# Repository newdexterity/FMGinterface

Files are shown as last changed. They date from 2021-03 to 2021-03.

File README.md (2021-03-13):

# A Wearable, Open-Source, Lightweight Forcemyography Armband: On Intuitive, Robust Muscle-Machine Interfaces
## Repository Contents
*	CAD files of the FSR based armband
*	ROS package to interface with the armband

## Force Sensitive Resistors based Armband

With an increasing number of robotic and prosthetic devices, there is a need for intuitive interfaces which enable the user to efficiently interact with them. The conventional interfaces are generally bulky and unsuitable for dynamic and unstructured environments. An alternative to the traditional interfaces is the class of Muscle-Machine Interfaces (MuMIs) that allow the user to have an embodied interaction with the devices they are controlling. In this work, we present a wearable, lightweight, FMG based armband for Human-Machine Interaction fabricated entirely out of 3D-printed parts and silicone components. The armband uses six force sensing units, each housing an FSR sensor. The capabilities of the armband are evaluated while decoding four different gestures (pinch, power, tripod, extension) and rest state and its performance is compared with a state-of-the-art electromyography (EMG) bioamplifier. The decoding performance of the decoding models trained on the data acquired from the armband is significantly better than the performance of the models trained on raw EMG data. The hardware design and the related processing software, are disseminated in an open-source manner.

### Components of the Band

The FMG band can be broken down into several smaller modules; the central control module, the strap module, and sensing modules. These components can be seen in Figure below. In total, there are currently six sensing modules evenly spaced around approximately 320˚ of the strap.

<p align="center">
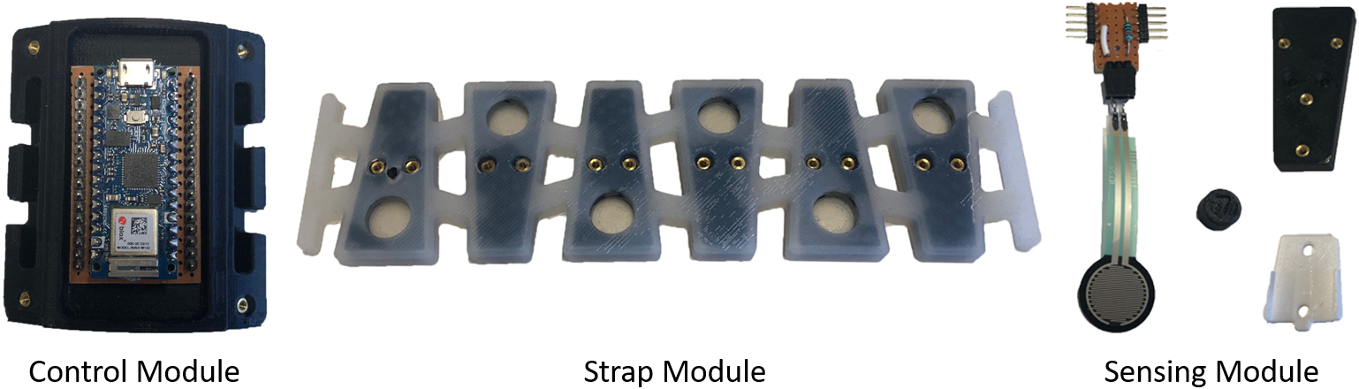
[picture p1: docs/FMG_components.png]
  
</p>

* The central control module, is responsible for collating all of the data from the sensors, and distributing it to an external device for post processing. An Arduino Nano 33 IoT micro-controller was used to collect the sensor data from the FSRs. This module also allows for the strap to be connected / disconnected, with a form fit keeping the components secured.
* The strap, is made from soft, flexible silicone and is embedded with 3D printed structural components that act as a frame to which the sensor modules are fixed to. This structural component has multiple holes that allow the silicone to cure around the part, ensuring no separation between the  component and the silicone occurs.
* The sensing modules, each contain a single Force Sensitive Resistor (FSR), accompanying circuitry, a transmission block, and a mounting plate for attaching the module to the band.

### Manufacturing Process

Each of the components in this device have been manufactured through Fused Deposition Manufacturing (FDM) processes such as 3D printing, or Hybrid Deposition Manufacturing (HDM).

A hybrid deposition manufacturing process was used to create the strap for the FMG band. A series of steps were employed as follows: First, the mould for the strap was manufactured through 3D printing, along with structural inserts. These components can be seen in the Figure below. A coating of mould release was applied to the mould to aid with removal of the strap. Next, threaded heat inserts were installed in the structural components, and secured to the strap mould with screws. Dragonskin 30 silicone was prepared and de-gassed, then poured into the mould. The mould was allowed to sit to ensure all gasses could escape the mould and allow the silicone to cure around the structural components. Once the silicone was cured, the structural components were unscrewed from the mould, and the completed strap removed.

<p align="center">
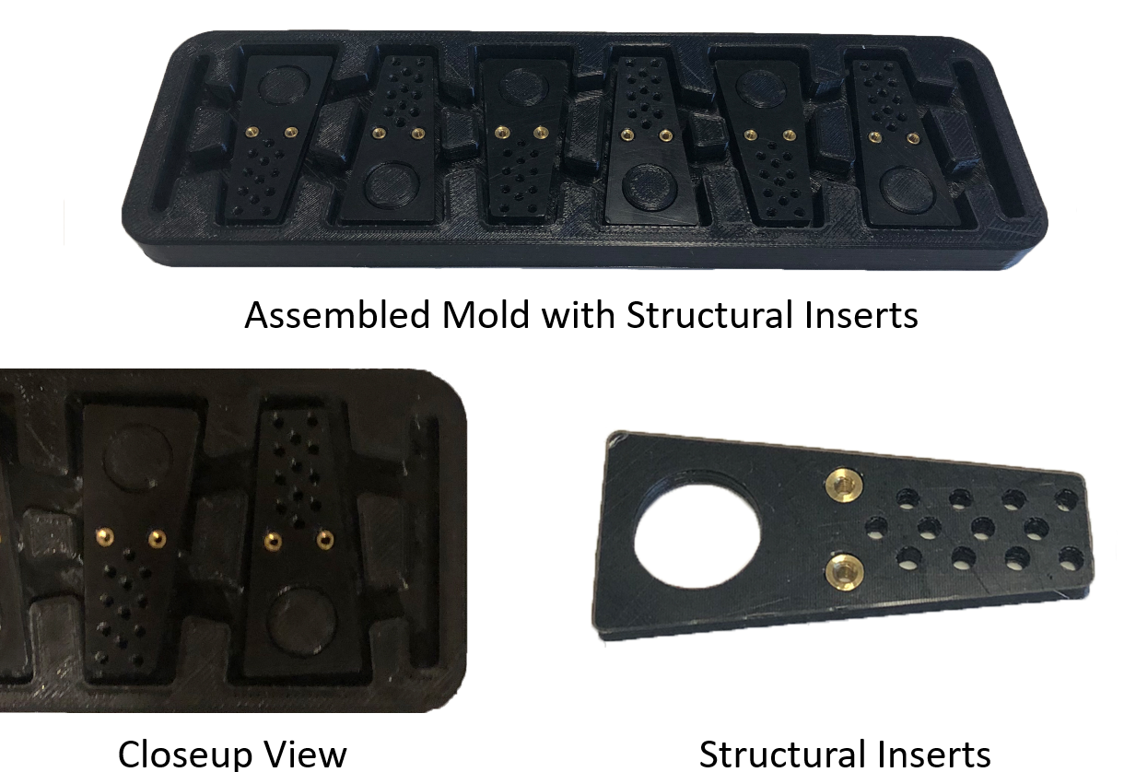
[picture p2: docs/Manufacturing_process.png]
  
</p>

The remaining components such as the micro-controller module and mounting components for the sensor modules were 3D printed. Threaded heat inserts were again used for securing the components together.

### Band Placement

The FMG band was placed in the upper half of the forearm where the majority of the muscle groups responsible for the movements of the digits are located. These muscle groups include extensor digitorum, flexor digitorum superficialis, flexor digitorum profundus, and flexor pollicis longus. Figure below shows the placement of the armband.

<p align="center">
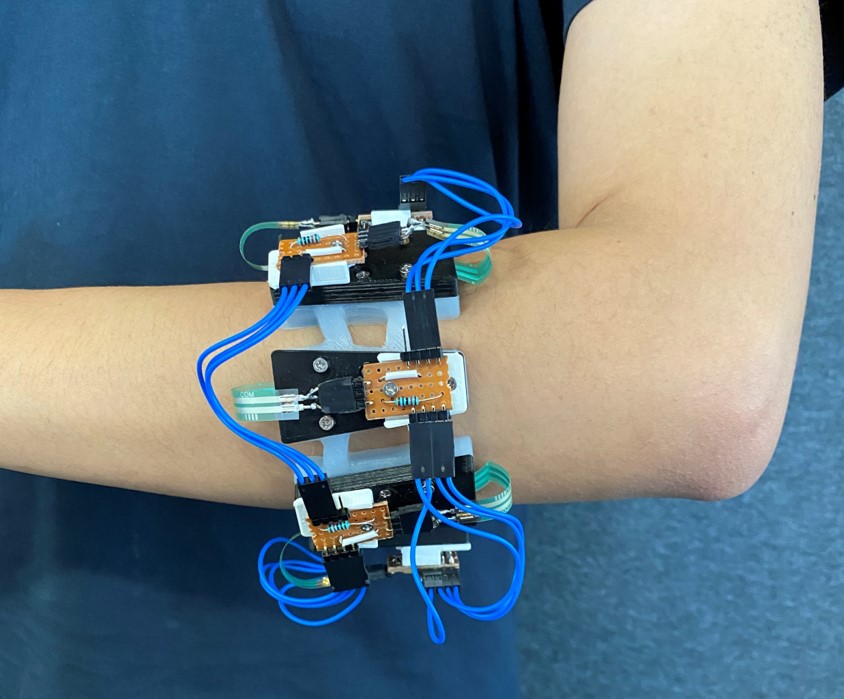
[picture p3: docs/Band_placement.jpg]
  
</p>

The performance of the armband was compared with state-of-the-art EMG bioamplifier. To do that, we compare the gesture decoding accuracy for the learning models developed using the data from the FMG armband, raw EMG data, and feature extracted EMG data. A time domain feature, Root Mean Square (RMS) value was extracted for each of the EMG channel. The RMS value represents the square root of the average power of the signal for the given time period. The RMS value is defined as:

<p align="center">
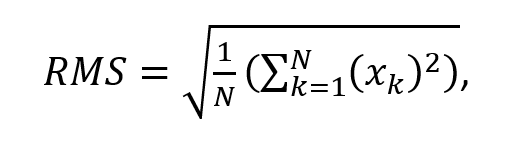
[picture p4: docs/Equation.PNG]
  
</p>

where N is the size of the window applied to the data. Figure below shows the FMG, raw EMG, and feature extracted EMG recordings during the pinch, power, tripod, and extension gestures. Subfigure a) shows the activation values for the FSR sensors, subfigure b) shows the raw EMG activations while subfigure c) shows the feature (RMS value) extracted value from the EMG signals.

<p align="center">
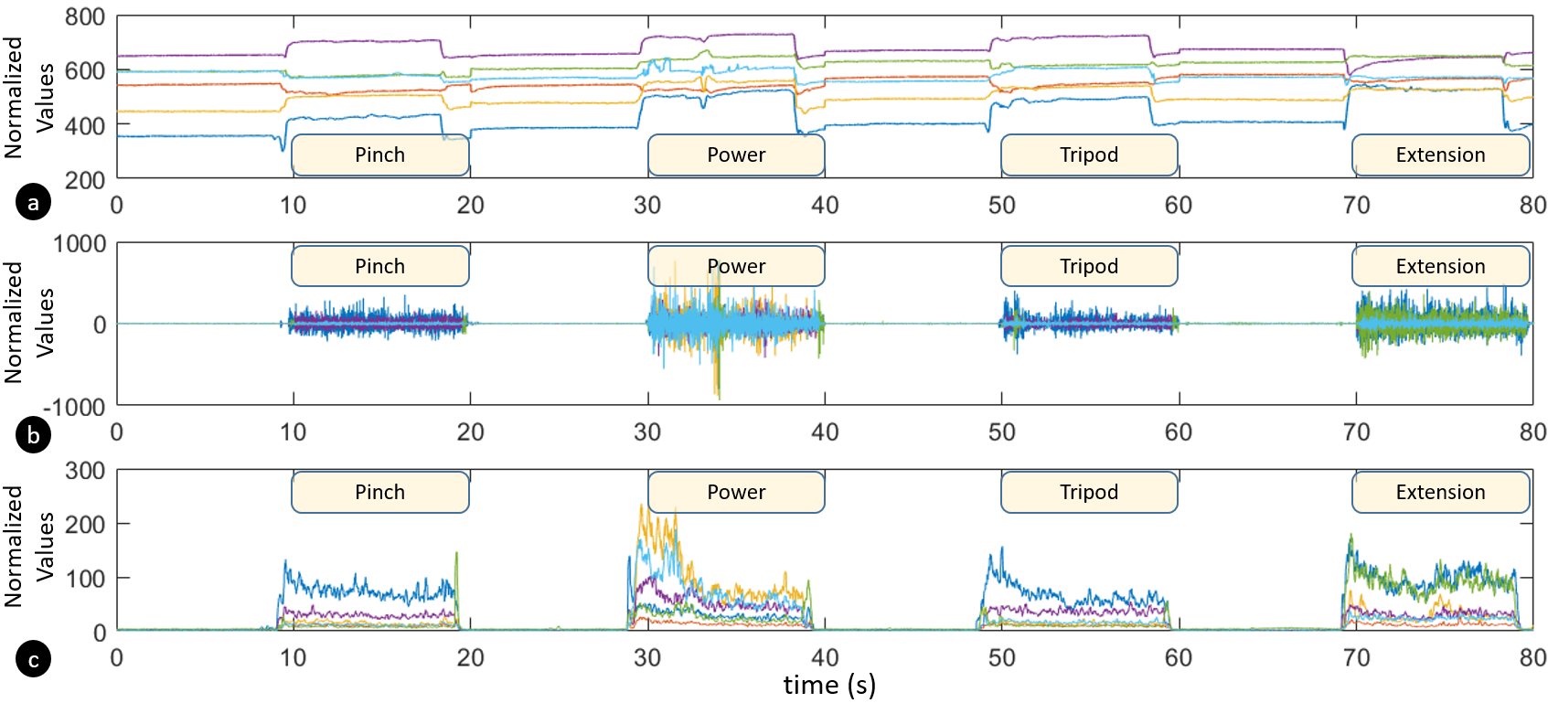
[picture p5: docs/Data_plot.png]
  
</p>

Table below shows the gesture decoding accuracy for each of the three datasets. It should be noted that the accuracy for the gesture decoding models is lowest for the ones developed using the data from raw EMG, while the accuracies for the models developed using the data from FMG and feature extracted EMG are comparable. However, using feature extracted EMG for developing the gesture decoding models introduce an extra step in computation, which might affect the real-time performance of the system.

<p align="center">
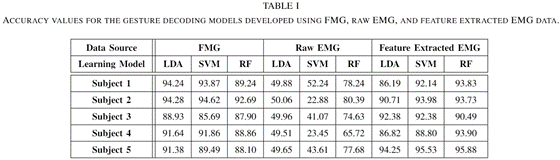
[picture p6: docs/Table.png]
  
</p>

To show an application of the proposed FMG armband, the gesture decoding model developed using the data collected for offline training was employed to decode the gestures in real-time and execute them on the NDX-A* robot hand. The demonstrations for the real-time gesture execution on the robot hand were recorded and the compiled video is available in HD quality at the following URL:

FMG Band video (https://youtu.be/6V1z5xVdlFU)

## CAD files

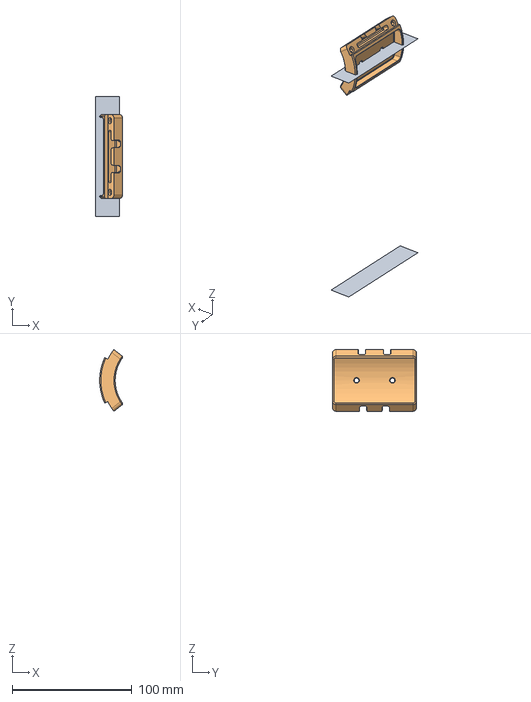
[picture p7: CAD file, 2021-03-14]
CAD/FSR_Band/STEP Files/fsr_central_unit.stp
22.7 x 100.0 x 245.9 mm

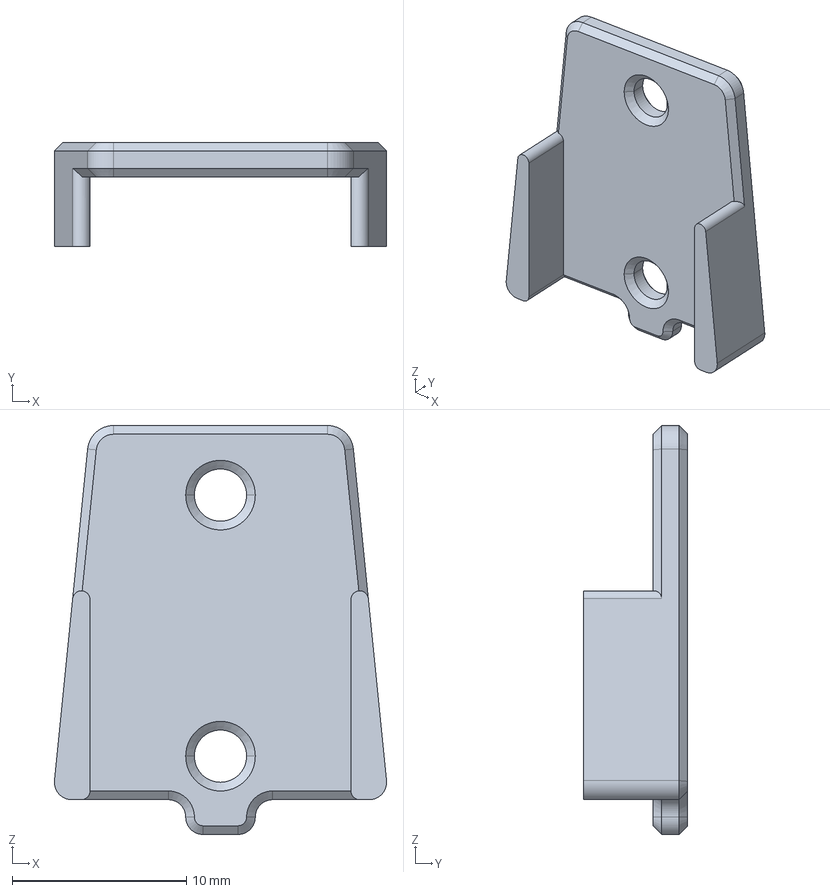
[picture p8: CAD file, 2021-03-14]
CAD/FSR_Band/STEP Files/fsr_pcb_mount.stp
19.1 x 6.00 x 23.5 mm

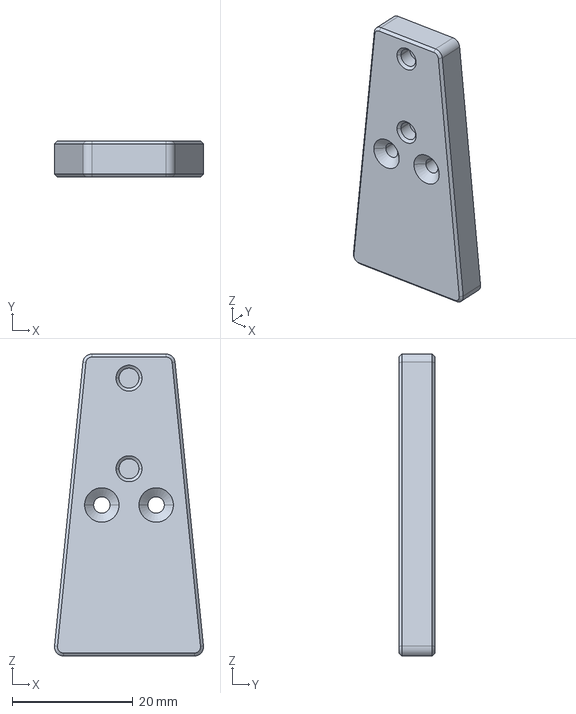
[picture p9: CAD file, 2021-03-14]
CAD/FSR_Band/STEP Files/fsr_sensor_cover.stp
24.7 x 6.00 x 50.0 mm

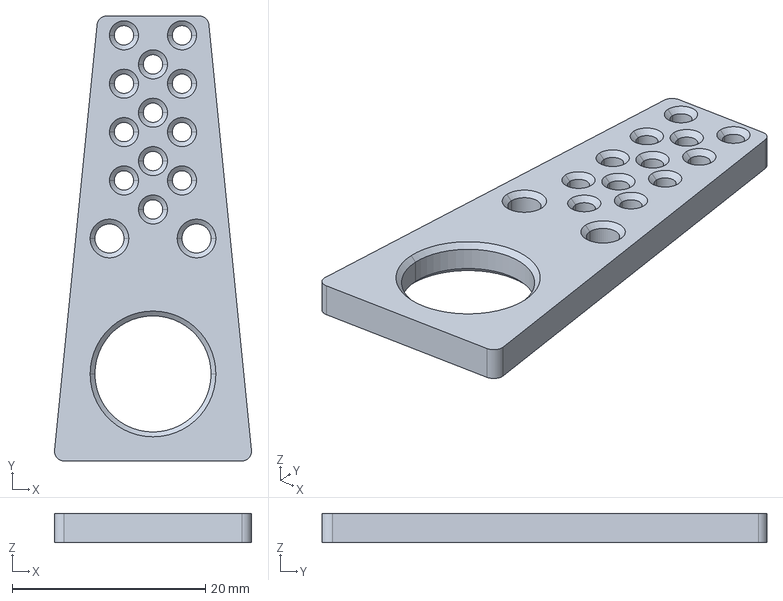
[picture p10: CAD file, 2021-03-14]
CAD/FSR_Band/STEP Files/fsr_structural_component.stp
20.4 x 46.0 x 3.00 mm

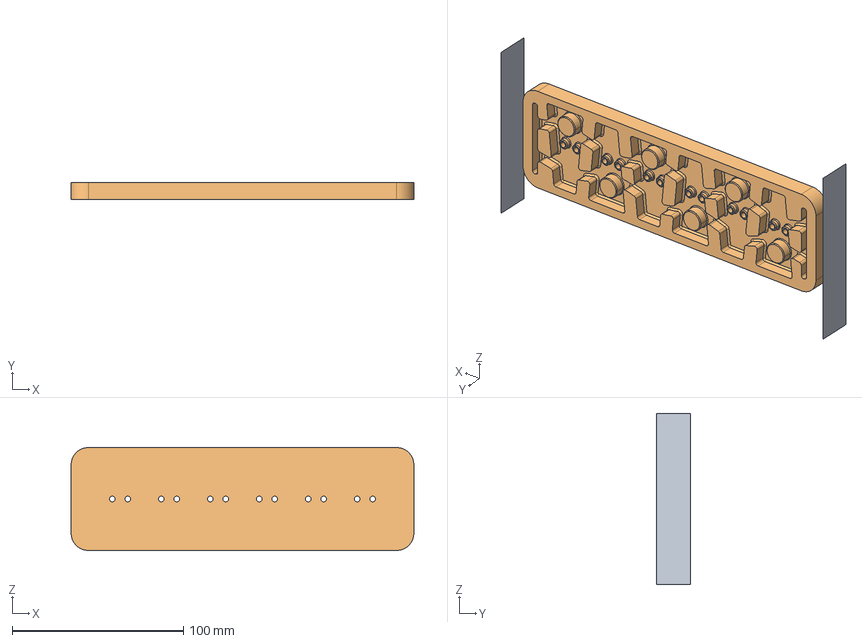
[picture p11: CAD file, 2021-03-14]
CAD/FSR_Band/STEP Files/fsr_strap_mold.stp
220.0 x 20.0 x 100.0 mm

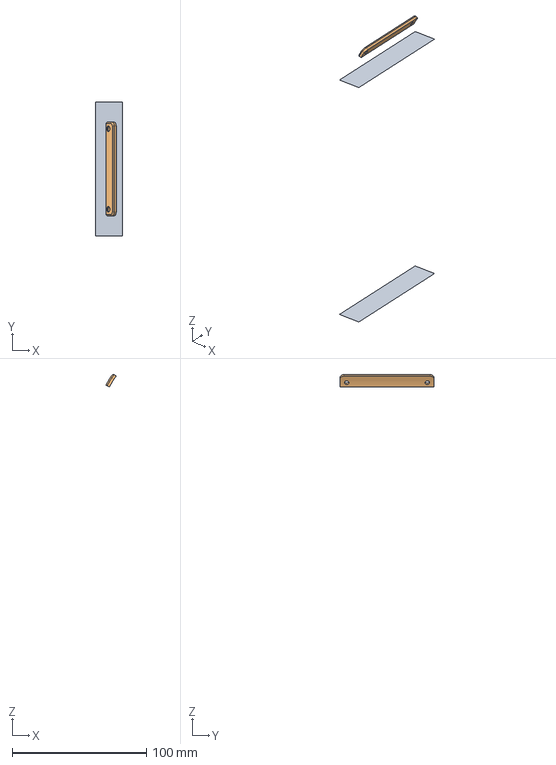
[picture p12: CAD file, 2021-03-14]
CAD/FSR_Band/STEP Files/fsr_strap_cover.stp
20.0 x 100.0 x 247.1 mm

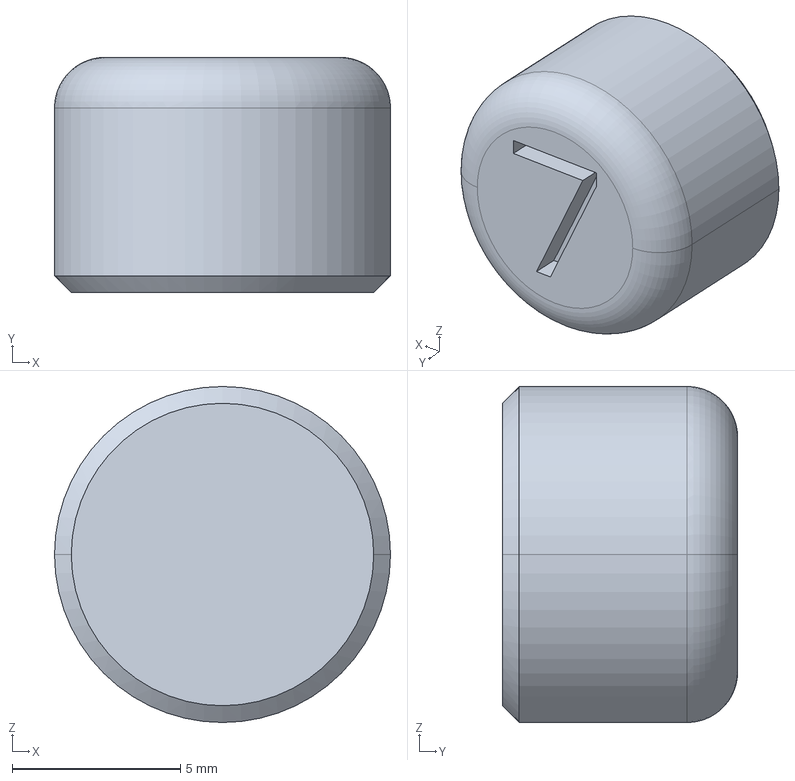
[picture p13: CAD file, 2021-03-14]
CAD/FSR_Band/STEP Files/fsr_disc_insert_7mm.stp
10.0 x 7.00 x 10.0 mm

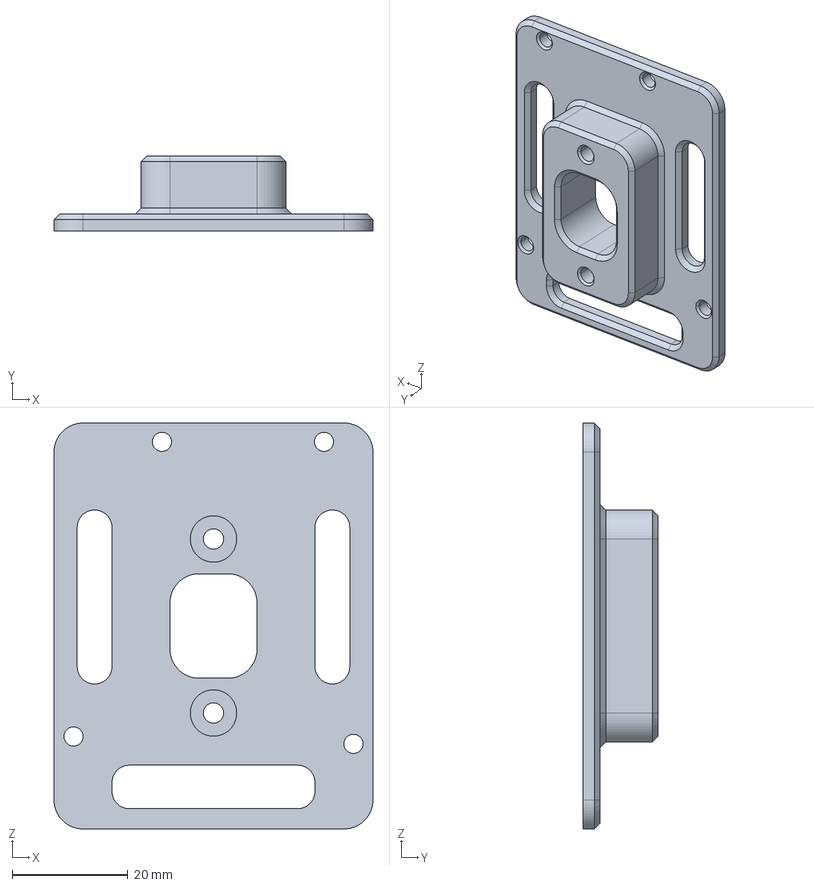
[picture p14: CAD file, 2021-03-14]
CAD/FSR_Band/STEP Files/uno_mount.stp
55.0 x 13.0 x 70.0 mm

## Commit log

2021-03-12 script files
    [test.csv]
2021-03-14 Armband step files
    [fsr_central_unit.stp, fsr_disc_insert_7mm.stp, fsr_pcb_mount.stp, fsr_sensor_cover.stp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]
2021-03-15 Upload arduino code
